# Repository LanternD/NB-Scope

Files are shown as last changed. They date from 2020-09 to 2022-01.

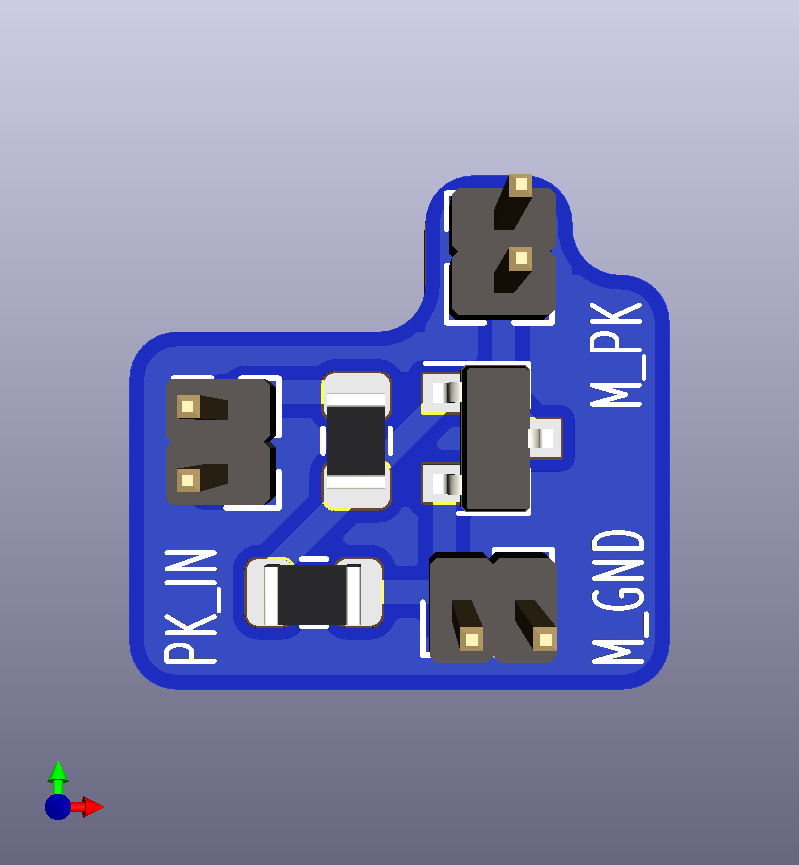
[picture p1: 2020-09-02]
Hardware/Auxilliary Boards/pwr_key_addon/pwr_key_addon.png

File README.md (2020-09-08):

# NB-Scope

Hardware and software design for NB-Scope.

NB-Scope is employed in our MobiCom 20 paper "Understanding Power Consumption of NB-IoT in the Wild: Tool and Large-scale Measuremen" [DOI](https://doi.org/10.1145/3372224.3419212).

Please check the README.md under the folders for more details.

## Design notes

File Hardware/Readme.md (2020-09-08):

# Hardware Guideline

## Overview

This folder contains the NB-Scope nodes hardware designs. Specifically, we have a folder for the mainboard, a folder for all the shieldboard for NB-Scope, and a folder for the auxilliary boards.

### Mainboard

The mainboard has 3 versions. **Please use ver 3.2**. The outdated versions are for reference only. They may work but not very stable. Ver 1.0 and 2.0 are not for NB-Scope projects, thus are omitted.

### Shieldboards

We have 7 types of shieldboard designs, supporting up to 9 types of different NB-IoT modules, including:

- Quectel BC28
- Quectel BC35
- Quectel BC26
- Quectel BC66
- Quectel BC95 (Not tested)
- Quectel BG36 (Not tested)
- Quectel BG96
- Gosuncn ME3616
- uBlox SARA-R410M-02B

(Quectel BG36/BG96 and Quectel BC35/BC95, have the same pin assignment, respectively.)

The module PCB project names should be straight-forward in the "Shieldboards" folder.

### Auxilliary boards

- Current sensing calibration board
- Firmware upgrade extension board
- Moulde benchmark extension board
- PWR_KEY addon

### Libraries

If you encounter missing symbol/footprint problem when opening the schematic or PCB files, please import them in the `Libraries` folder. The missing libraries should be a subset of the available footprints.

### Materials

I put the related documents related to hardware design here, including NB-IoT module summary and various datasheets.

## EDA environment

The software to open the projects is [KiCad](https://kicad-pcb.org/) (Pronounced as "key-cad").

PLEASE use the **Nightly-build** version of KiCad because the projects are created by that. The projects are not backward compatible.

To open the 3D viewer, click "View->3D Viewer" (<kbd>⌥+3</kbd> on Mac or <kbd>Alt+3</kbd> on other operating systems) in the `Pcbnew` software menu.

If you use the latest version of KiCad to open `.sch` files, `Eeschema`, the software component to edit schematic, will ask you to convert the `.sch` into `.kicad_sch`. Just go ahead and follow the instruction in KiCad.

You can generate all the files for fabrication in `Pcbnew` software module in KiCad.

## Project structure

- `<project_name>.pro`: project main file.
- `<project_name>.sch` or `<project_name>.kicad_sch`: project schematic design. If `.sch` and `.kicad_sch` co-exist, use the `.kicad_sch` one.
- `<project_name>.kicad_pcb`: project PCB design.
- `Exported Files` folder: exported/generated files from the projects, including Gerber files, bill of materials (BOM), positioning files (for SMT process), and other board 3D views or documents. I suggest you double check the project schematic and pcb designs, then generate these fabrication files again by yourself, instead of sending the Gerber files to manufacturers directly.

There are some KiCad generated backup or middle files. I forget to remove them before committing. You may ignore or edit them. They have the following patterns:

- `fp-info-cache`
- `<project name>-cache.lib`
- `<project name>-rescue.dcm`
- `<project name>-rescue.lib`
- `<project name>.kicad_pcb-bak`
- `<project name>.sch-bak`
- `sys-lib-table`

## Click into their corresponding folders for more details

If you have any questions, please send me an email to "yangdeli at msu.edu".

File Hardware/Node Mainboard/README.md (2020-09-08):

# Introduction

Node mainboard is responsible for hosting the module shieldboard, sensing the environment, collecting debug log and current traces, and so on.

Major components on the board: 

- STM32F103 as the main processor
- LM3671-3.3 as DC-DC converter
- CM1624 as micro SD card protector
- CAT24C128 as non-volatile memory
- TXB0108 as logic level converter (3.3v <-> 1.8v)
- Si7021 as temperature and relative humidity sensor
- INA226 as current sensor

It is powered by one or two 18650 batteries. It also supports USB 5V as the input voltage, using jumper cap to switch.

# Important Notes

## Components

- Pin headers. For the two rows hosting the NB-IoT UE shieldboard and the power jumpper, please use 1.27 mm pitch connectors. For all the other 1.27 mm throughhole connectors with 3-6 pins, use 1.25 mm pitch connectors. Please take a look at the photo of Ver 3.1 below. Please find the datasheet in "[Hardware/Materials](../Materials/A1251.pdf)" folder. Male connector: A1251H-XP; Female connector: A1251WV-XP. Note: this is just an example. You don't need to use the exact component.
- The 1.25mm pitch connectors could be converted to 2.54 mm pitch pins to connect to other components, such as ST-Link programmer.
- USB connector. There are many similar USB connectors available, please take a look at their size and shape and ensure they match. "Molex-105017-0001" would work but it is expensive. 
- Battery holder. One thing that is not shown in the picture is the battery holder, whose model is "BK-18650-PC4". You need to solder this **after everything else**, because the battery holder will block the access to whole bottom layer.

## NB-IoT UE Pin Assignment

The pin assignment should be taken care for future module shieldboard design.

Module Pin Assignment

Note: the labels starting with `M_` means the pins are treated as part of the module. For example, `M_MAIN_UART_TX` means the UART Tx of the module, which should be connected to the MCU UART Rx pin accordingly.

`Left_Conn` means the upper row in the picture below, `Right_conn` is the bottom row accordingly.

The module ground GNDs are aggregated to 4 pins on the `Right_conn`, which passes through a current sampling resistor on the mainboard.

# Known Issues

- If you use the generic ST-Link V2 dongle as programmer, do not use it to power the board alone, otherwise the LM3671 buck converter chip will burn. 

  **Correct way**: Power on the board using 18650 battery or 5V USB, then plug on the ST-Link debugger. After you finish programming/debugging, unplug ST-Link V2 FIRST, and then shutdown the board power.

- I didn't add the ESD protection to the board, so please ensure the ESD on the hand is largely removed before touching the board.

**Note**: Ver 3.1 and 3.0 have other minor issues, which were largely fixed in Ver 3.2. Please see the "Change Log" below. To save your time, do not use Ver 3.0 and 3.1.

- The "Module USB" can use as the 5V input of the board, while the "MCU USB" cannot do it. If you want to use the latter one to power the board, connect the "+5V" near it to the "+5V" near the "PWR SELECT" pin header.

# Suggestions in Mainboard Hardware Design

The latest version (ver 3.2) of mainboard generally works well, but I have several important suggestions for future design. 

1. Upgrade the power chip. LM3671 supports a maximum current of 600 mA, which sometimes has little margin for some NB-IoT modules. So I suggest using other power IC, such as LM3281 or TPS62160.
2. The STM32F103 does not have DMA channel for SD card writing, which means you cannot do anything else when writing the SD card. My suggestion is to use another STM32 chip. You need to double check in STM32 CubeMX whether the chip supports DMA channel in SDIO interface.
3. Add the ESD protection circuit.
4. Add a fuse to the power module.

# Gallery

## Ver 3.2

Node Mainboard v3.2
Node Mainboard v3.2

Note: the two shieldboard rows should be pin socket, instead of pin header. They are interchangeable though.

## Ver 3.1

Node Mainboard v3.1
Node Mainboard v3.1
Node Mainboard v3.1

## Ver 3.0

Node Mainboard v3.0
Node Mainboard v3.0

# Change Log

## Ver 3.2

- Added a DTC143Z to control the PWRKEY pin for uBlox SARA-R410M-02B and Quectel BG96, BC26, and BC66, such that we don't need the `pwr_key_add_on` modification board for these modules.
- Replaced the labels in schematic by another type (with an enclosure), which shows the direction of the signal.
- Added a power jumper to isolate the DC-DC module with other components on the board, for easier debugging.
- Used a smaller form factor transistor (DTC143Z) for LED control.
- Added a 1.5k pull-up resistor for USB connector.
- Removed the BOOT0 control header. Connected BOOT0 to GND by default. Added a pad for connecting to 3.3V by jumper wire temporarily. 
- Used a better matching footprint for all the buttons.
- Reduced the SWD connector from 6 pins to 4 pins.

## Ver 3.1

- Updated the power module. Replaced the large inductor to a smaller one. The power module layout was also improved.
- Replaced the resistor array in micro SD card protetion circuit with CM1624.
- Updated the layout of the user buttons.

## Ver 3.0

Actually the first version of NB-Scope mainboard.

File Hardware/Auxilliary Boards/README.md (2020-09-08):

# Introduction

Auxilliary boards are used to extend the capability of the mainboard and shieldboard, as well as to calibrate the current sensors.

# Current Calibration Board

Since the 0.1 Ohm current sensing resistors are different, the current sensing should be calibrated as per mainboard. 

You need a series of resistors for this board. The actual resistance does not matter. We just compare the sensor reading with the digital multimeter or power monitor reading.

## How to calibrate

calibration guide

Solder the 1.27 mm pitch headers according to the image above. Then follow the instruction to test the output.

Before calibration, make sure the embedded code runs the "current sensing demo" (`void run_demo8_i_bus_sensing()` in `Software/field-test-control/Src/fm_demo.c`). Check the `main.c` as well. 

The mainboard should be connected to the PC via USB, then the PC should open a serial console to read the data from the board.

Steps:

1. See the figure above.
2. See the figure above.
3. Read and record the external current measurement device output (mA).
4. Read and record the INA226 output via the USB UART. The board will output the current register reading once per second.
5. Repeat the above steps for resistors from 13.3 Ohm to 165 Ohm. The 11 Ohm is not recommended. Do not try the 5.6 Ohm.
6. Calculation as follows:
  
  1. Multiply the register value by 0.018311 to get the current reading of INA226. (Note: if the output is already the current value, you don't need to do this conversion, depending on the output of the embedded program.)
  2. Divide the INA226 current by the meter reading current to get a ratio.
  3. Multiply the ratio with 2778 (the preset INA226 calibration register value) to get the new calibration register value. 
  4. Average all the calibration values to get the final calibration value.
  
Here is a table showing the measurement and calculation example for one of our board.

| Expected current (mA) | Meter reading (mA) | INA226 register reading | Calculated INA226 current (mA) | New calibration value |
|-----------------------|--------------------|-------------------------|--------------------------------|-----------------------|
|                    20 |               20.0 |                    1089 |                      19.940679 |              2786.264 |
|                  48.5 |               49.0 |                    2659 |                      48.688949 |              2795.747 |
|                   100 |               99.5 |                    5484 |                     100.417524 |              2752.517 |
|                   150 |              149.0 |                    8235 |                     150.791085 |              2745.003 |
|                   200 |              198.0 |                   10974 |                     200.944914 |              2737.287 |
|                   248 |                244 |                   13487 |                     246.960457 |              2744.699 |

The final calibration value is the average of the last column, resulting in 2760.

The value you get should not be too far from these value above. The final calibration value is around 2700 - 2900. For the same batch of boards, the standard deviation is less than 50. If you use a different batch of current sensing resistor, the value can deviate up to 150. 

**The new current calibration value should be written into the onboard EEPROM before node deployment.**

Note: you need to calibrate EVERY mainboard.

# Module Benchmark Extension Board

An upgraded version of "Firmware Upgrade Extension Board". It docks the shieldboard for the "real-time benchmark mode" of NB-Scope. It can be used to upgrade the NB-IoT module firmware as well. Basically it pinouts all the necessary connectivity of the UE module, such that we can connect them to other peripherals, such as power monitor and UART. 

The two pin headers are compatible with the mainboard.

The "EXT3V3" is used to connect to the power monitor. For example, the RED terminal of the monitor is connected to the EXT3V3, and the BLACK terminal is connected to the 3V3, repectively. "EXTGND" is likewise.

# Firmware Upgrade Extension Board

This is the predecessor of "Module Benchmark Extension Board". Generally you can ignore this one.

# PWRKEY Addon

A tiny board that simply has a BJT on it. It is used to fixed the PWRKEY pin on the UE modules before ver 3.2 mainboard. If you use the latest version of the mainboard, you can ignore this.

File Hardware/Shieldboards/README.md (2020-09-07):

# Important Note

- The majority of the modules here can be soldered by hand, except Quectel BG96 and uBlox SARA-R410M-02B.
  - If you solder the SARA-R410M-02B **by yourself** (customizing the stencil and applying the solder paste), instead of using the SMT service, you need to shrink the size of all the pads of the SARA-R410M-02B footprint! Otherwise they are likely to get short-circuited.
  - Before
  
  SARA footprint before
  - After
  
  SARA footprint after
  
- All the shieldboards have a RESET button for the module.
- There is a design compatibility issue in those modules with a "PWR_KEY" pin, including SARA-R410M-02B, BG96, BC26, and BC66. The pin requires an open collector transistor to enable, which I use different hardware designs to take care of it across different version of the board. Here is the summary:
  - Node mainboard v3.2 + BC26/BC66/SARA shieldboard: no modification needed.
  - Node mainboard v3.2 + SARA shieldboard: use GPIO_L4 as the `PWRKEY` control pin. The software code can handle this.
  - Node mainboard v3.1 + BC26/BC66/BG96 shieldboard: need to fixed by the `pwr_key_addon` in "Auxilliary Boards" folder (**Not recommended**).
  - Node mainboard v3.1 + SARA shieldboard: use GPIO_L4 as the `PWRKEY` control pin (**Not recommended**).

# Photos

Note: the pin headers in the photos face up, but in reality they should be soldered on the other side of the board, facing down, such that the shieldboard can be docked to the mainboard.

## Quectel BC26 (BC66) Shieldboard

BC26 Shiledboard
BC26 Shiledboard

Note: BC66 is almost identical to BC26 board, except for the swap between UART Tx and Rx pin.

## Quectel BC28 Shieldboard

BC28 Shiledboard
BC28 Shiledboard

## Quectel BC95/BC35 Shieldboard

BC95 Shiledboard
BC95 Shiledboard

## Gosuncn ME3616 Shieldboard

ME3616 Shiledboard
ME3616 Shiledboard

## Quectel BG96/BG36 Shieldboard

BG96 Shiledboard
BG96 Shiledboard

## uBlox SARA-R410M-02B Shieldboard

SARA Shiledboard
SARA Shiledboard

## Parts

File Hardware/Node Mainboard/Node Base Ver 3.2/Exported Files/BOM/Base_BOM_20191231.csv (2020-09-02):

Id | Designator | Package | Quantity | Designation | Supplier and ref
1 | REF**,REF** | test_pad | 2 | test_pad
2 | REF** | WEEE-Logo_4.2x6mm_SilkScreen | 1 | WEEE-Logo_4.2x6mm_SilkScreen
3 | REF** | ESD-Logo_6.6x6mm_SilkScreen | 1 | ESD-Logo_6.6x6mm_SilkScreen
4 | U1 | SMF05C | 1 | SMF05C
5 | J6 | PinSocket_1x04_P1.27mm_Vertical | 1 | SWD_Conn
6 | H1 | 18650_Battery_Holder_2x | 1 | Battery_Holder_2x
7 | TP2 | test_pad | 1 | 3.3V_OUT
8 | TP1 | test_pad | 1 | 3.3VPU
9 | SW3 | SMD_Switch | 1 | SW_2
10 | SW2 | SMD_Switch | 1 | SW_1
11 | SW1 | SMD_Switch | 1 | SW_RST
12 | R15 | R_0603_1608Metric | 1 | 1.5k
13 | R4,R8,R7 | R_0603_1608Metric | 3 | 10k
14 | J2 | PinHeader_2x02_P1.27mm_Vertical | 1 | 3.3V ISO
15 | Q2,Q1 | SOT-723 | 2 | DTC143Z
16 | U8 | UDFN-16_3.3x1.35mm_0.4Pitch | 1 | CM1624
17 | REF** | test_pad | 1 | SW
18 | R14,R5 | R_0603_1608Metric | 2 | 0
19 | L1 | L_Sumida_CDRH2D14_3.2x3.2x1.55mm | 1 | 2.2uH
20 | C9 | C_0805_2012Metric | 1 | 10uF
21 | C8 | C_0805_2012Metric | 1 | 4.7uF
22 | G*** | Cat-Logo | 1 | LOGO
23 | C20,C19,C18,C16,C13,C12,C11,C10 | C_0603_1608Metric | 8 | 100nF
24 | Y1 | Crystal_SMD_5032-2Pin_5.0x3.2mm | 1 | 8MHz
25 | D1,D4,D3,D2 | LED_0805_2012Metric | 4 | LED
26 | J8 | PinHeader_1x03_P2.54mm_Vertical | 1 | PWR_SELECT
27 | J4 | PinSocket_1x04_P1.27mm_Vertical | 1 | Display_Connector
28 | R16,R13,R11,R3 | R_0603_1608Metric | 4 | 4.7k
29 | RN4 | R_Array_Convex_4x0603 | 1 | 2.2k
30 | U7 | USON-20_2x4mm_P0.4mm | 1 | TXB0108DQSR
31 | T1 | test_pad | 1 | M_ADC
32 | R21,R20,R10,R9 | R_0603_1608Metric | 4 | 22
33 | R2 | R_0603_1608Metric | 1 | 470k
34 | R1 | R_0603_1608Metric | 1 | 220k
35 | J10,J5 | USB_Micro-B_Molex-105017-0001 | 2 | USB_B_Micro
36 | J9 | PinSocket_1x03_P1.27mm_Vertical | 1 | AUX_UART
37 | J7 | PinSocket_1x06_P1.27mm_Vertical | 1 | GPIO_Out
38 | J3 | TF_Card_Socket | 1 | Micro_SD_Card
39 | C17,C15,C14,C7,C1 | C_0603_1608Metric | 5 | 10nF
40 | C5,C4,C3,C2 | C_0603_1608Metric | 4 | 10pF
41 | Y2 | Crystal_SMD_3215-2Pin_3.2x1.5mm | 1 | 32.768kHz
42 | U6 | DFN-6-1EP_3x3mm_P1mm_EP1.5x2.4mm | 1 | Si7021-A20
43 | U5 | VSSOP-10_3x3mm_P0.5mm | 1 | INA226
44 | U4 | TSOT-23-5 | 1 | LM3671MF-3.3
45 | U3 | SOIC-8_3.9x4.9mm_P1.27mm | 1 | CAT24C128
46 | U2 | LQFP-64_10x10mm_P0.5mm | 1 | STM32F103RETx
47 | R12 | R_1206_3216Metric | 1 | R100
48 | J13 | PinHeader_1x22_P1.27mm_Vertical | 1 | Right_Conn
49 | J12 | PinHeader_1x22_P1.27mm_Vertical | 1 | Left_Conn
50 | J1 | Nano Sim Socket 1.1H, 6P | 1 | SIM_Card

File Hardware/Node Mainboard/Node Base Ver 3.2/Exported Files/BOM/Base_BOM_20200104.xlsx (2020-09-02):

Id | Need Soldering | Unit Price | Price for one Board | Designator | Package | Quantity | Designation | Supplier and ref | Datasheet
1 | N |  |  | REF**,REF** | test_pad | 2 | test_pad
2 | N |  |  | REF** | WEEE-Logo_4.2x6mm_SilkScreen | 1 | WEEE-Logo_4.2x6mm_SilkScreen
3 | N |  |  | REF** | ESD-Logo_6.6x6mm_SilkScreen | 1 | ESD-Logo_6.6x6mm_SilkScreen
4 | Y |  |  | U1 | SMF05C | 1 | SMF05C | SMF05CT1G
5 | N |  |  | J6 | PinSocket_1x04_P1.27mm_Vertical | 1 | SWD_Conn
6 | N |  |  | H1 | 18650_Battery_Holder_2x | 1 | Battery_Holder_2x
7 | N |  |  | TP2 | test_pad | 1 | 3.3V_OUT
8 | N |  |  | TP1 | test_pad | 1 | 3.3VPU
9 | Y |  |  | SW3 | SMD_Switch | 1 | SW_2 | TSA363G25-250B White_3*6*2.5 | https://item.szlcsc.com/330468.html
10 | Y |  |  | SW2 | SMD_Switch | 1 | SW_1 | TSA363G25-250H Red_3*6*2.5 | https://item.szlcsc.com/330467.html
11 | Y |  |  | SW1 | SMD_Switch | 1 | SW_RST | 1TS002B-1700-5001-CT | https://item.szlcsc.com/300328.html
12 | Y |  |  | R15 | R_0603_1608Metric | 1 | 1.5k
13 | Y |  |  | R4,R8,R7 | R_0603_1608Metric | 3 | 10k
14 | Y |  |  | J2 | PinHeader_2x02_P1.27mm_Vertical | 1 | 3.3V ISO | Trimmed from: | https://item.szlcsc.com/44374.html
15 | Y |  |  | Q2,Q1 | SOT-723 | 2 | DTC043ZM | DTC043ZMT2L | http://rohmfs.rohm.com/en/products/databook/datasheet/discrete/transistor/digital/dtc043zmt2l-e.pdf
16 | Y |  |  | U8 | UDFN-16_3.3x1.35mm_0.4Pitch | 1 | CM1624 | CM1624-08DE | https://www.mouser.com/ProductDetail/ON-Semiconductor/CM1624-08DE?qs=sGAEpiMZZMvbyeSUH4qH%2FG%252BWhnbEq2Sg
17 | N |  |  | REF** | test_pad | 1 | SW
18 | Y |  |  | R14,R5 | R_0603_1608Metric | 2 | 0
19 | Y |  |  | L1 | L_Sumida_CDRH2D14_3.2x3.2x1.55mm | 1 | 2.2uH | CDRH2D14NP-2R2NC | https://www.mouser.com/ProductDetail/851-CDRH2D14NP-2R2NC
20 | Y |  |  | C9 | C_0805_2012Metric | 1 | 10uF | JMK212BJ106KG-T
21 | Y |  |  | C8 | C_0805_2012Metric | 1 | 4.7uF | JMK212BJ475KG-T
22 | N |  |  | G*** | Cat-Logo | 1 | LOGO
23 | Y |  |  | C20,C19,C18,C16,C13,C12,C11,C10 | C_0603_1608Metric | 8 | 100nF
24 | Y |  |  | Y1 | Crystal_SMD_5032-2Pin_5.0x3.2mm | 1 | 8MHz | CX5032GA08000H0PST02
25 | Y |  |  | D1,D4,D3,D2 | LED_0805_2012Metric | 4 | LED | LTST-C170KRKT red | Color is flexible
26 | Y |  |  | J8 | PinHeader_1x03_P2.54mm_Vertical | 1 | PWR_SELECT |  | https://item.szlcsc.com/50265.html
27 | N |  |  | J4 | PinSocket_1x04_P1.27mm_Vertical | 1 | Display_Connector
28 | Y |  |  | R16,R13,R11,R3 | R_0603_1608Metric | 4 | 4.7k
29 | Y |  |  | RN4 | R_Array_Convex_4x0603 | 1 | 2.2k | CAY16-222J4LF
30 | Y |  |  | U7 | USON-20_2x4mm_P0.4mm | 1 | TXB0108DQSR | TXB0108DQSR
31 | N |  |  | T1 | test_pad | 1 | M_ADC
32 | Y |  |  | R21,R20,R10,R9 | R_0603_1608Metric | 4 | 22
33 | Y |  |  | R2 | R_0603_1608Metric | 1 | 470k
34 | Y |  |  | R1 | R_0603_1608Metric | 1 | 220k
35 | Y |  |  | J10,J5 | USB_Micro-B_Molex-105017-0001 | 2 | USB_B_Micro | Molex 105017-0001 | https://www.molex.com/webdocs/datasheets/pdf/en-us/1050170001_IO_CONNECTORS.pdf
36 | N |  |  | J9 | PinSocket_1x03_P1.27mm_Vertical | 1 | AUX_UART
37 | N |  |  | J7 | PinSocket_1x06_P1.27mm_Vertical | 1 | GPIO_Out
38 | Y |  |  | J3 | TF_Card_Socket | 1 | Micro_SD_Card | TF-015 | https://item.szlcsc.com/114441.html
39 | Y |  |  | C17,C15,C14,C7,C1 | C_0603_1608Metric | 5 | 10nF
40 | Y |  |  | C5,C4,C3,C2 | C_0603_1608Metric | 4 | 10pF
41 | Y |  |  | Y2 | Crystal_SMD_3215-2Pin_3.2x1.5mm | 1 | 32.768kHz | NX3215SA-32.768K-STD-MUS-2
42 | Y |  |  | U6 | DFN-6-1EP_3x3mm_P1mm_EP1.5x2.4mm | 1 | Si7021-A20 | SI7021-A20-GM1R
43 | Y |  |  | U5 | VSSOP-10_3x3mm_P0.5mm | 1 | INA226 | INA226AIDGSR
44 | Y |  |  | U4 | TSOT-23-5 | 1 | LM3671MF-3.3 | LM3671MF-3.3/NOPB
45 | Y |  |  | U3 | SOIC-8_3.9x4.9mm_P1.27mm | 1 | CAT24C128 | CAT24C128WI-GT3
46 | Y |  |  | U2 | LQFP-64_10x10mm_P0.5mm | 1 | STM32F103RETx | STM32F103RET6
47 | Y |  |  | R12 | R_1206_3216Metric | 1 | R100 | CRM1206AFX-R100ELF
48 | Y |  |  | J13 | PinSocket_1x22_P1.27mm_Vertical | 1 | Right_Conn | Can be trimmed from 1*50 etc. | Example https://item.taobao.com/item.htm?id=530374128662&ns=1&abbucket=18
49 | Y |  |  | J12 | PinSocket_1x22_P1.27mm_Vertical | 1 | Left_Conn | Can be trimmed from 1*50 etc. | Example https://item.taobao.com/item.htm?id=530374128662&ns=1&abbucket=18
50 | Y |  |  | J1 | Nano Sim Socket 1.1H, 6P | 1 | SIM_Card | Molex 104224-0820

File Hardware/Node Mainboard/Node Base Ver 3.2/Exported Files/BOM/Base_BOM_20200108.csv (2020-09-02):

Id | Designator | Package | Quantity | Designation | Supplier and ref
1 | U1 | SOT-363_SC-70-6 | 1 | SMF05C
2 | J13 | PinHeader_1x22_P1.27mm_Vertical | 1 | Right_Conn
3 | J12 | PinHeader_1x22_P1.27mm_Vertical | 1 | Left_Conn
4 | REF**,REF** | test_pad | 2 | test_pad
5 | REF** | WEEE-Logo_4.2x6mm_SilkScreen | 1 | WEEE-Logo_4.2x6mm_SilkScreen
6 | REF** | ESD-Logo_6.6x6mm_SilkScreen | 1 | ESD-Logo_6.6x6mm_SilkScreen
7 | J6 | PinSocket_1x04_P1.27mm_Vertical | 1 | SWD_Conn
8 | H1 | 18650_Battery_Holder_2x | 1 | Battery_Holder_2x
9 | TP2 | test_pad | 1 | 3.3V_OUT
10 | TP1 | test_pad | 1 | 3.3VPU
11 | SW3 | SMD_Switch | 1 | SW_2
12 | SW2 | SMD_Switch | 1 | SW_1
13 | SW1 | SMD_Switch | 1 | SW_RST
14 | R15 | R_0603_1608Metric | 1 | 1.5k
15 | R4,R8,R7 | R_0603_1608Metric | 3 | 10k
16 | J2 | PinHeader_2x02_P1.27mm_Vertical | 1 | 3.3V ISO
17 | Q2,Q1 | SOT-723 | 2 | DTC143Z
18 | U8 | UDFN-16_3.3x1.35mm_0.4Pitch | 1 | CM1624
19 | REF** | test_pad | 1 | SW
20 | R14,R5 | R_0603_1608Metric | 2 | 0
21 | L1 | L_Sumida_CDRH2D14_3.2x3.2x1.55mm | 1 | 2.2uH
22 | C9 | C_0805_2012Metric | 1 | 10uF
23 | C8 | C_0805_2012Metric | 1 | 4.7uF
24 | G*** | Cat-Logo | 1 | LOGO
25 | C20,C19,C18,C16,C13,C12,C11,C10 | C_0603_1608Metric | 8 | 100nF
26 | Y1 | Crystal_SMD_5032-2Pin_5.0x3.2mm | 1 | 8MHz
27 | D1,D4,D3,D2 | LED_0805_2012Metric | 4 | LED
28 | J8 | PinHeader_1x03_P2.54mm_Vertical | 1 | PWR_SELECT
29 | J4 | PinSocket_1x04_P1.27mm_Vertical | 1 | Display_Connector
30 | R16,R13,R11,R3 | R_0603_1608Metric | 4 | 4.7k
31 | RN4 | R_Array_Convex_4x0603 | 1 | 2.2k
32 | U7 | USON-20_2x4mm_P0.4mm | 1 | TXB0108DQSR
33 | T1 | test_pad | 1 | M_ADC
34 | R21,R20,R10,R9 | R_0603_1608Metric | 4 | 22
35 | R2 | R_0603_1608Metric | 1 | 470k
36 | R1 | R_0603_1608Metric | 1 | 220k
37 | J10,J5 | USB_Micro-B_Molex-105017-0001 | 2 | USB_B_Micro
38 | J9 | PinSocket_1x03_P1.27mm_Vertical | 1 | AUX_UART
39 | J7 | PinSocket_1x06_P1.27mm_Vertical | 1 | GPIO_Out
40 | J3 | TF_Card_Socket | 1 | Micro_SD_Card
41 | C17,C15,C14,C7,C1 | C_0603_1608Metric | 5 | 10nF
42 | C5,C4,C3,C2 | C_0603_1608Metric | 4 | 10pF
43 | Y2 | Crystal_SMD_3215-2Pin_3.2x1.5mm | 1 | 32.768kHz
44 | U6 | DFN-6-1EP_3x3mm_P1mm_EP1.5x2.4mm | 1 | Si7021-A20
45 | U5 | VSSOP-10_3x3mm_P0.5mm | 1 | INA226
46 | U4 | TSOT-23-5 | 1 | LM3671MF-3.3
47 | U3 | SOIC-8_3.9x4.9mm_P1.27mm | 1 | CAT24C128
48 | U2 | LQFP-64_10x10mm_P0.5mm | 1 | STM32F103RETx
49 | R12 | R_1206_3216Metric | 1 | R100
50 | J1 | Nano Sim Socket 1.1H, 6P | 1 | SIM_Card

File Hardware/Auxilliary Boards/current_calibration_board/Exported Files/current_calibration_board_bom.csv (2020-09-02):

Id | Designator | Package | Quantity | Designation | Supplier and ref
1 | REF** | KiCad-Logo2_5mm_SilkScreen | 1 | KiCad-Logo2_5mm_SilkScreen
2 | G*** | Cat-Logo | 1 | LOGO
3 | J6 | PinHeader_1x03_P2.54mm_Vertical | 1 | GND_Conn
4 | R8 | Resistor_SMD_1225_2W | 1 | 5.6
5 | R7 | R_2512_6332Metric_Pad1.52x3.35mm_HandSolder | 1 | 11
6 | R6 | R_2512_6332Metric_Pad1.52x3.35mm_HandSolder | 1 | 13.3
7 | R5 | R_2512_6332Metric_Pad1.52x3.35mm_HandSolder | 1 | 16.5
8 | R4 | R_1210_3225Metric_Pad1.42x2.65mm_HandSolder | 1 | 22
9 | R3 | R_1210_3225Metric_Pad1.42x2.65mm_HandSolder | 1 | 33
10 | R2 | R_1206_3216Metric_Pad1.42x1.75mm_HandSolder | 1 | 68
11 | R1 | R_0805_2012Metric_Pad1.15x1.40mm_HandSolder | 1 | 165
12 | J5 | PinHeader_1x08_P2.54mm_Vertical | 1 | Conn_01x08
13 | J4 | PinHeader_1x03_P2.54mm_Vertical | 1 | Vcc_Conn
14 | J3 | PinHeader_1x04_P1.27mm_Vertical | 1 | GND_Conn
15 | J2,J1 | PinHeader_1x03_P1.27mm_Vertical | 2 | Vcc_Conn

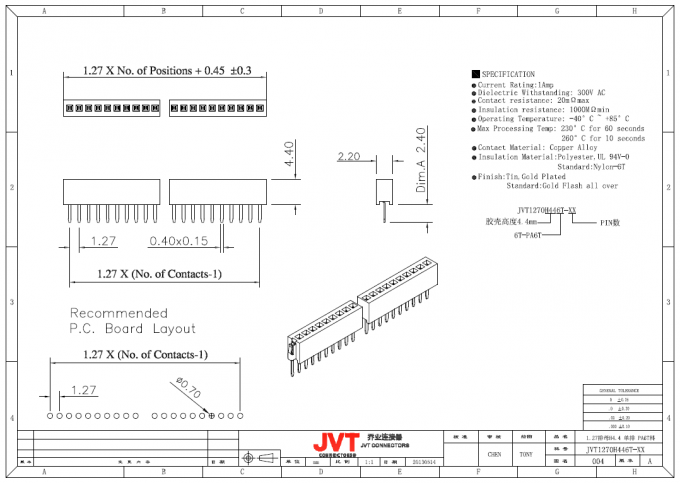
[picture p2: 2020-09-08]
Hardware/Materials/1.27 pin socket.png

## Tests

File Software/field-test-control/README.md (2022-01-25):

# Field Test Control

Embedded code that runs on STM32F103RET6, hosting a bunch of peripherals. It performs the NB-IoT field measurement task.

Note: the "`fm_`" in the code means "field measurement".

# MCU Software version log

- 00001: 20200111. Code is ready for BC28/BC26/ME3616. Migrating to BG96.
- 00002:

# Design 

## MCU

- STM32F103RETx. 72MHz 512kB Flash, 64kB RAM.
- High speed external (HSE) crystal oscillator: 8MHz, cap: 10 pF.
- LSE crystal oscillator: 32.768kHz, cap: 10 pF, high quality ceramic cap.
- No pull-up resistor needed for **RESET**.
- I2C pull-up resistor = 4.7 kOhm.
- SDIO freq max: 48 MHz.

### Pin Connection

- TF (SDIO)

	39 PC8 <-> TF 7 SDIO_D0
	40 PC9 <-> TF 8 SDIO_D1
	51 PC10 <-> TF 1 SDIO_D2
	52 PC11 <-> TF 2 SDIO_D3
	53 PC12 <-> TF 5 SDIO_CLK
	54 PD2 <-> TF 3 SDIO_CMD

- SWD (MCU debug port)

	46 PA13 SWD_IO <-> SWD_IO
	49 PA14 SWD_CLK<-> SWD_CLK
	55 PB3 SWO <-> SWO

- Temperature & humidity sensor, EEPROM (share the same I2C)

  29 PB10 I2C2_SCL <-> Si7021 Sensor_SCL, EEPROM_SCL
  30 PB11 I2C2_SDA <-> Si7021 Sensor_SDA, EEPROM_SDA

- INA226 current sensor

  58 PB6 I2C1_SCL <-> INA226_SCL
  59 PB7 I2C1_SDA <-> INA226_SDA

- MCU USB

  44 PA11 USBDM <-> Connector USB DM
  45 PA12 USBDP <-> Connector USB DP

- Misc.

16 PA2 USART2_Tx <-> Module Main UART Rx
17 PA3 USART2_Rx <-> Module Main UART Tx
42 PA9 USART1_Tx <-> Module Debug UART Rx
43 PA10 USART1_Rx <-> Module Debug UART Tx

8 PC0 ADC123_IN10 <-> V_batt ADC

33 PB12 SPI2_NSS <-> Module SPI_CS
34 PB13 SPI2_SCK <-> Module SPI_CLK / I2S_CK
35 PB14 SPI2_MISO <-> Module SPI2_MISO
36 PB15 SPI2_MOSI <-> Module SPI2_MOSI

9 PC1 <-> GPIO_L1
10 PC2 <-> PSM_IND
11 PC3 <-> GPIO_L2
14 PA0 <-> GPIO_L3
15 PA1 <-> GPIO_L4
20 PA4 <-> Module PWRKEY
21 PA5 <-> Module RESET
22 PA6 <-> Module PSM external wakeup interruption
23 PA7 <-> AP_READY
50 PA15 <-> GPIO_R1
41 PA8 <-> GPIO_R2
38 PC7 <-> GPIO_R3
37 PC6 <-> Module RI

- Not used by module:

26 PB0 <-> SWITCH_1
27 PB1 <-> SWITCH_2
56 PB4 <-> TF_DETECT (Ext GPIO_1)
57 PB5 <-> Ext GPIO_2
61 PB8 <-> Ext GPIO_3
62 PB9 <-> Ext GPIO_4
24 PC4 <-> LED 0 on board
25 PC5 <-> LED 1 on board
2 PC13 <-> Not Connected

### Logic Convertion on Base Board

- Main UART Tx/Rx
- AUX UART Tx/Rx
- Debug UART Tx/Rx
- RI

### I2C Address

- INA226: 7 byte address is 0x80. with I2C1
- SI7021: 7 byte address is 0x40. with I2C2. After adding the r/w bit, should be 0x81 and 0x80;
- CAT24C128: 7 byte address is 0x54. with I2C2.
- SSD1306 display: 7 byte address is 0x78. with I2C2.

### EEPROM Storage Design

There are 256 pages available, 64 Bytes each. So the total capacity is 256\*64 = 16382 Bytes = 128 Kbits.

- Global Variables:
	- Last running mode

- Demo page
	- 0x2000 - 0x2003: uint32_t wakeup times from sleeping.
	- 0x2004 - 0x2004: uint8_t seconds to sleep (for RTT configuration).

## TF Card

Need pull-up 25 kOhm, serial 40 Ohm: CLK, CMD, Data0, Data1, Data2, Data3

Convex resistor array CAY16-223J8LF

# Current Sensing INA226

- Use Kelven connection!
- LSB for shunt voltage: fixed 2.5 uV.
- Calculation example:
	- Current LSB value = 0.8/2^15 = 0.000024414 = 24.414 uA
	- Calibration registor = 0.00512/(CurrentLSB\*ShuntResistor) = 0.00512 / (0.000024414\*0.05) = 4194
	- Example: Assume current_truth = 0.2A, R_shunt=0.05 Ohm, then shunt voltage = 10mV. ShuntVReg = 10mV/2.5uV=4000. current_calc = ShuntV\*CalibrationReg/2048 = 4000\*4194/2048 \* Current LSB = 8191 \* Current LSB=8191\*0.000024414=0.199984 A.
- Choose 100 mOhm resistor.

## Current sensing calibration

As the shunt resistor has resistant variation, we need to calibrate it. Here's how to get the calibration register value:

- The shunt resistor on board is 100 mOhm.
- Determine the max possible current: I_max = 0.6A
- Calculate the current LSB: current_lsb = I_max / 2^15 = 0.6/2^15 = **0.018311** mA/bit <= **Fix this number!**
- According to the 7.5.1 Eq(3) in the datasheet: CurrentRegister = ShuntVoltage * CalibrationReg / 2048
- I_acutal = CurrentRegister * current_lsb
- Accoarding to Eq(1), calbirationReg_theoretical = 0.00512 / (current_lsb*R_shunt) = 0.00512 / (0.018311/1000*0.1) = 2796.1
- **Assume** the calibrationReg = 2778 (according to the calibration measurement on an actual circuit board)
- CalibrationReg_New / CalibrationReg_Old (which is 2778) = multimeter_current_reading / current_reading_from_INA226 = multimeter_current_reading / (CurrentReg_Old * current_lsb)
- **Example**: CurrentReg (use USB VCP to check) is 13543, Multiply this by 0.018311, you get an INA226 current reading = 248 mA. Next, the multimeter reading is 246.0 mA. So 248/246 = CalibrationReg_New/2778 => we have CalibrationReg_New = 2778*248/246 = 2800.
- Update INA226_CALIB_VAL in ti_ina226.h Line32 with the new caibration register 2800
- Check that the new current reading is more accurate.

# Modules

- Need to convert 3.3v to 1.8v (bidirectional): BC26, BC66, BG96, SARA R410M 02B
- Need to convert 3.3v to 3.0v (bidirectional): BC28, BC35, BC95
- Left side: 16 pins
- Right side: 10 pins

# Programming Task Lists

- RTT clock signal configuration
- [x] Battery voltage sensing
- Sleep and wake-up
- Watch-dog
- Temperature and humidity sensor reading
- [x] EEPROM writing and reading (share the same I2C with the sensor)
- Current sensing
- TF card read/write through SDIO
- AT Command control API
- Server configuration
- Debug log reading
- Debug log FSM
- (\*) DMA: current I2C to SDIO

------

# Links

- current sensor resistors

	[10 mOhm](https://www.mouser.com/ProductDetail/ROHM-Semiconductor/PMR100HZPFU10L0?qs=sGAEpiMZZMtlleCFQhR%2FzZdCyObyGWxusWWJKncYy0Q%3D)
	[100 mOhm](https://www.mouser.com/ProductDetail/Bourns/CRM1206AFX-R100ELF?qs=sGAEpiMZZMtlleCFQhR%2FzXAGiOCRCr1IaXP90uykHS56ie6t3FxO7w%3D%3D)

- tf card socket

	http://www.klsele.com/products/connectors/641/4975.html

- Resistor array 8X

	- [8X 22kOhm](https://www.mouser.com/ProductDetail/Bourns/CAY16-223J8LF?qs=sGAEpiMZZMvrmc6UYKmaNe77kisCPsGdUuiwPEa9T%2FU%3D)
	- [4X 2.2kOhm](https://www.mouser.com/ProductDetail/Bourns/CAY16-222J4LF?qs=sGAEpiMZZMvrmc6UYKmaNUApqJ%252B%2FEZrJ%2FpdW56SM27Q%3D)
	- [8X 43 Ohm](https://www.mouser.com/ProductDetail/Bourns/CAY16-430J4LF?qs=sGAEpiMZZMukHu%252BjC5l7YZZvIpUe0TuoDMVA%252BgU2smk%3D)

- 8MHz Crystal Oscillator

	https://detail.tmall.com/item.htm?spm=a230r.1.14.11.6bc4917d8fGEWE&id=36990674059&cm_id=140105335569ed55e27b&abbucket=13

# Future

- [x] Replace the pull-up resistors and protection circuits for SD card with On Semiconductor **CM1624**.
- [x] Redesign the 3.3 V converter circuit.
- [ ] Isolate the 3.3 V power output with the circuit power (with a jumper cap).
- [ ] Add a 1.5k pull-up resistor at MCU USB D+. (Must Have)
- [ ] The PWR_KEY pin should not go though the TXB0108. Move this part to the base board with a transistor.

# Module Board

[Impedance Calculator](https://chemandy.com/calculators/coplanar-waveguide-with-ground-calculator.htm)

Fr4 material. Relative permittivity=4.4. The board thickness is chosen as 1 mm. The trace thickness is 1.35 mil for 1oz copper. 

Microstrip: the trace width should be **1.83~1.87** mm.
Coplanar: the gap width should be **0.3 mm**, the track width is **1.29 mm**.

# Module specific AT commands

## BG96

- Set once
    + Scan sequence
        * AT+QCFG="nwscanmode",3,1
        * AT+QCFG="iotopmode",1,1
        * AT+QCFG="band",1,1,180A,11

- AT+QPSMS?
    + +QPSMS: 1,,,"46800","2880"  // network side parameters.

## SARA R410M-02B 

GPIO assignment: 

- Pin16, M_NET_LED
- Pin19, SARA_GPIO1
- Pin23, SARA_GPIO2
- Pin24, SARA_GPIO3
- Pin25, SARA_STATUS_LED
- Pin42, SIM_DET

AT Command

These command is needed for only **ONCE**.

- Set pin function (Page 168)
  - AT+UGPIOC=16,2
  - AT+UGPIOC=25,10
  - AT+UGPIOC=42,7
  
- Set searchable bands (reboot to take effect)
  - AT+UBANDMASK=0,0,0
  - AT+UBANDMASK=1,6154,0 (only search Band 2, 4, 12, 13)
  
- Select RAT
  - AT+URAT=8 // NB-IoT only

- PDP context definition

  - 

- PSM setting
    + AT+CPSMS=1,,,"00101100","00000001"  // For all the USA modules. (except BC66)
    + 12 hours PSM, 2 seconds idle.
    + Default: +CPSMS:0,,,"00011000","00001010"
    
The belows need to be set every round.

- Cell Info (Not supported)

  - AT+UCGED=5
  - AT+UCGED?

# BC66

- Set the CGDEFCONT (PDP context)
  - AT+QCGDEFCONT="IP","mw01.vzwstatic"  // for new models

Default CPSMS: +CPSMS: 1,,,"00100011","00100010"
  - AT+CPSMS=1,,,"00100011","00100010"  // This is the default
  - AT+CPSMS=1,,,"00100011","00000101"  // new: idle 10 seconds.

- Set baudrate
    + AT+IPR=115200  // fixed rate
    + AT&W  // write to NVM

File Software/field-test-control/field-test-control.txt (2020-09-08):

Configuration	field-test-control
STM32CubeMX 	5.4.0
Date	09/08/2020
MCU	STM32F103RETx

PERIPHERALS	MODES	FUNCTIONS	PINS
ADC1	IN10	ADC1_IN10	PC0
I2C1	I2C	I2C1_SCL	PB6
I2C1	I2C	I2C1_SDA	PB7
I2C2	I2C	I2C2_SCL	PB10
I2C2	I2C	I2C2_SDA	PB11
RCC	Crystal/Ceramic Resonator	RCC_OSC_IN	PD0-OSC_IN
RCC	Crystal/Ceramic Resonator	RCC_OSC_OUT	PD1-OSC_OUT
RCC	Crystal/Ceramic Resonator	RCC_OSC32_IN	PC14-OSC32_IN
RCC	Crystal/Ceramic Resonator	RCC_OSC32_OUT	PC15-OSC32_OUT
RTC	Activate Clock Source	RTC_VS_RTC_Activate	VP_RTC_VS_RTC_Activate
SDIO	SD 4 bits Wide bus	SDIO_CK	PC12
SDIO	SD 4 bits Wide bus	SDIO_CMD	PD2
SDIO	SD 4 bits Wide bus	SDIO_D0	PC8
SDIO	SD 4 bits Wide bus	SDIO_D1	PC9
SDIO	SD 4 bits Wide bus	SDIO_D2	PC10
SDIO	SD 4 bits Wide bus	SDIO_D3	PC11
SPI2	Full-Duplex Master	SPI2_MISO	PB14
SPI2	Full-Duplex Master	SPI2_MOSI	PB15
SPI2	Full-Duplex Master	SPI2_SCK	PB13
SYS	Serial Wire	SYS_JTCK-SWCLK	PA14
SYS	Serial Wire	SYS_JTMS-SWDIO	PA13
SYS	SysTick	SYS_VS_Systick	VP_SYS_VS_Systick
USART1	Asynchronous	USART1_RX	PA10
USART1	Asynchronous	USART1_TX	PA9
USART2	Asynchronous	USART2_RX	PA3
USART2	Asynchronous	USART2_TX	PA2
USB	Device (FS)	USB_DM	PA11
USB	Device (FS)	USB_DP	PA12

Pin Nb	PINs	FUNCTIONs	LABELs
3	PC14-OSC32_IN	RCC_OSC32_IN	
4	PC15-OSC32_OUT	RCC_OSC32_OUT	
5	PD0-OSC_IN	RCC_OSC_IN	
6	PD1-OSC_OUT	RCC_OSC_OUT	
8	PC0	ADC1_IN10	V_BATT_ADC
9	PC1	GPIO_Output	M_GPIO_L1
10	PC2	GPIO_Input	M_PSM_IND
11	PC3	GPIO_Output	M_GPIO_L2
14	PA0-WKUP	GPIO_Output	M_GPIO_L3
15	PA1	GPIO_Output	M_GPIO_L4
16	PA2	USART2_TX	
17	PA3	USART2_RX	
20	PA4	GPIO_Output	M_PWRKEY
21	PA5	GPIO_Output	M_RESET
22	PA6	GPIO_Output	M_WAKEUP_FROM_PSM
23	PA7	GPIO_Output	M_AP_READY
24	PC4	GPIO_Output	LED0
25	PC5	GPIO_Output	LED1
26	PB0	GPIO_EXTI0	BUTTON1
27	PB1	GPIO_EXTI1	BUTTON2
29	PB10	I2C2_SCL	BUS_SCL
30	PB11	I2C2_SDA	BUS_SDA
33	PB12	GPIO_Output	M_SPI_CS
34	PB13	SPI2_SCK	
35	PB14	SPI2_MISO	
36	PB15	SPI2_MOSI	
37	PC6	GPIO_Input	M_RI
38	PC7	GPIO_Output	M_GPIO_R3
39	PC8	SDIO_D0	
40	PC9	SDIO_D1	
41	PA8	GPIO_Output	M_GPIO_R2
42	PA9	USART1_TX	
43	PA10	USART1_RX	
44	PA11	USB_DM	
45	PA12	USB_DP	
46	PA13	SYS_JTMS-SWDIO	
49	PA14	SYS_JTCK-SWCLK	
50	PA15	GPIO_Output	M_GPIO_R1
51	PC10	SDIO_D2	
52	PC11	SDIO_D3	
53	PC12	SDIO_CK	
54	PD2	SDIO_CMD	
55	PB3*	SYS_JTDO-TRACESWO	
56	PB4	GPIO_Input	TF_DET
57	PB5	GPIO_Output	GPIO_2
58	PB6	I2C1_SCL	INA226_SCL
59	PB7	I2C1_SDA	INA226_SDA
61	PB8	GPIO_Output	GPIO_3
62	PB9	GPIO_Output	GPIO_4
PERIPHERALS	MODES	FUNCTIONS	PINS
ADC1	IN10	ADC1_IN10	PC0
I2C1	I2C	I2C1_SCL	PB6
I2C1	I2C	I2C1_SDA	PB7
I2C2	I2C	I2C2_SCL	PB10
I2C2	I2C	I2C2_SDA	PB11
RCC	Crystal/Ceramic Resonator	RCC_OSC_IN	PD0-OSC_IN
RCC	Crystal/Ceramic Resonator	RCC_OSC_OUT	PD1-OSC_OUT
RCC	Crystal/Ceramic Resonator	RCC_OSC32_IN	PC14-OSC32_IN
RCC	Crystal/Ceramic Resonator	RCC_OSC32_OUT	PC15-OSC32_OUT
RTC	Activate Clock Source	RTC_VS_RTC_Activate	VP_RTC_VS_RTC_Activate
SDIO	SD 4 bits Wide bus	SDIO_CK	PC12
SDIO	SD 4 bits Wide bus	SDIO_CMD	PD2
SDIO	SD 4 bits Wide bus	SDIO_D0	PC8
SDIO	SD 4 bits Wide bus	SDIO_D1	PC9
SDIO	SD 4 bits Wide bus	SDIO_D2	PC10
SDIO	SD 4 bits Wide bus	SDIO_D3	PC11
SPI2	Full-Duplex Master	SPI2_MISO	PB14
SPI2	Full-Duplex Master	SPI2_MOSI	PB15
SPI2	Full-Duplex Master	SPI2_SCK	PB13
SYS	Serial Wire	SYS_JTCK-SWCLK	PA14
SYS	Serial Wire	SYS_JTMS-SWDIO	PA13
SYS	SysTick	SYS_VS_Systick	VP_SYS_VS_Systick
USART1	Asynchronous	USART1_RX	PA10
USART1	Asynchronous	USART1_TX	PA9
USART2	Asynchronous	USART2_RX	PA3
USART2	Asynchronous	USART2_TX	PA2
USB	Device (FS)	USB_DM	PA11
USB	Device (FS)	USB_DP	PA12

Pin Nb	PINs	FUNCTIONs	LABELs
3	PC14-OSC32_IN	RCC_OSC32_IN	
4	PC15-OSC32_OUT	RCC_OSC32_OUT	
5	PD0-OSC_IN	RCC_OSC_IN	
6	PD1-OSC_OUT	RCC_OSC_OUT	
8	PC0	ADC1_IN10	V_BATT_ADC
9	PC1	GPIO_Output	M_GPIO_L1
10	PC2	GPIO_Input	M_PSM_IND
11	PC3	GPIO_Output	M_GPIO_L2
14	PA0-WKUP	GPIO_Output	M_GPIO_L3
15	PA1	GPIO_Output	M_GPIO_L4
16	PA2	USART2_TX	
17	PA3	USART2_RX	
20	PA4	GPIO_Output	M_PWRKEY
21	PA5	GPIO_Output	M_RESET
22	PA6	GPIO_Output	M_WAKEUP_FROM_PSM
23	PA7	GPIO_Output	M_AP_READY
24	PC4	GPIO_Output	LED0
25	PC5	GPIO_Output	LED1
26	PB0	GPIO_EXTI0	BUTTON1
27	PB1	GPIO_EXTI1	BUTTON2
29	PB10	I2C2_SCL	BUS_SCL
30	PB11	I2C2_SDA	BUS_SDA
33	PB12	GPIO_Output	M_SPI_CS
34	PB13	SPI2_SCK	
35	PB14	SPI2_MISO	
36	PB15	SPI2_MOSI	
37	PC6	GPIO_Input	M_RI
38	PC7	GPIO_Output	M_GPIO_R3
39	PC8	SDIO_D0	
40	PC9	SDIO_D1	
41	PA8	GPIO_Output	M_GPIO_R2
42	PA9	USART1_TX	
43	PA10	USART1_RX	
44	PA11	USB_DM	
45	PA12	USB_DP	
46	PA13	SYS_JTMS-SWDIO	
49	PA14	SYS_JTCK-SWCLK	
50	PA15	GPIO_Output	M_GPIO_R1
51	PC10	SDIO_D2	
52	PC11	SDIO_D3	
53	PC12	SDIO_CK	
54	PD2	SDIO_CMD	
55	PB3*	SYS_JTDO-TRACESWO	
56	PB4	GPIO_Input	TF_DET
57	PB5	GPIO_Output	GPIO_2
58	PB6	I2C1_SCL	INA226_SCL
59	PB7	I2C1_SDA	INA226_SDA
61	PB8	GPIO_Output	GPIO_3
62	PB9	GPIO_Output	GPIO_4

SOFTWARE PROJECT

Project Settings : 
Project Name : field-test-control
Project Folder : /Users/dlyang/Dropbox/field-test-control
Toolchain / IDE : SW4STM32
Firmware Package Name and Version : STM32Cube FW_F1 V1.8.0

Code Generation Settings : 
STM32Cube MCU packages and embedded software packs : Copy only the necessary library files
Generate peripheral initialization as a pair of '.c/.h' files per peripheral : No
Backup previously generated files when re-generating : No
Delete previously generated files when not re-generated : Yes
Set all free pins as analog (to optimize the power consumption) : No

Toolchains Settings : 
Compiler Optimizations :

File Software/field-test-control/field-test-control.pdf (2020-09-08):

## field-test-control Project Configuration Report

# 1. Description

## 1.1. Project

Project Name | field-test-control
Board Name | custom
Generated with: | STM32CubeMX 5.4.0
Date | 09/08/2020

## 1.2. MCU

MCU Series | STM32F1
MCU Line | STM32F103
MCU name | STM32F103RETx
MCU Package | LQFP64
MCU Pin number | 64

# 2. Pinout Configuration

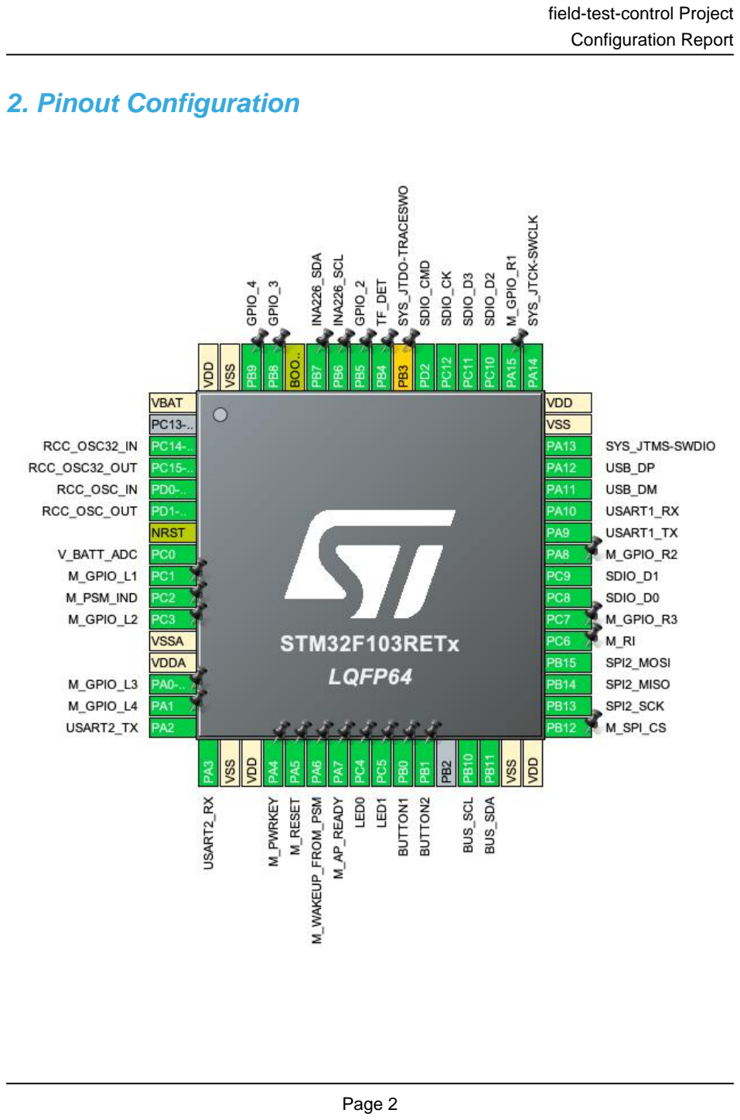
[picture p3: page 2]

# 3. Pins Configuration

Pin Number LQFP64 | Pin Name (function after reset) | Pin Type | Alternate Function(s) | Label
1 | VBAT | Power
3 | PC14-OSC32_IN | I/O | RCC_OSC32_IN
4 | PC15-OSC32_OUT | I/O | RCC_OSC32_OUT
5 | PD0-OSC_IN | I/O | RCC_OSC_IN
6 | PD1-OSC_OUT | I/O | RCC_OSC_OUT
7 | NRST | Reset
8 | PC0 | I/O | ADC1_IN10 | V_BATT_ADC
9 | PC1 * | I/O | GPIO_Output | M_GPIO_L1
10 | PC2 * | I/O | GPIO_Input | M_PSM_IND
11 | PC3 * | I/O | GPIO_Output | M_GPIO_L2
12 | VSSA | Power
13 | VDDA | Power
14 | PA0-WKUP * | I/O | GPIO_Output | M_GPIO_L3
15 | PA1 * | I/O | GPIO_Output | M_GPIO_L4
16 | PA2 | I/O | USART2_TX
17 | PA3 | I/O | USART2_RX
18 | VSS | Power
19 | VDD | Power
20 | PA4 * | I/O | GPIO_Output | M_PWRKEY
21 | PA5 * | I/O | GPIO_Output | M_RESET
22 | PA6 * | I/O | GPIO_Output | M_WAKEUP_FROM_PSM
23 | PA7 * | I/O | GPIO_Output | M_AP_READY
24 | PC4 * | I/O | GPIO_Output | LED0
25 | PC5 * | I/O | GPIO_Output | LED1
26 | PB0 | I/O | GPIO_EXTI0 | BUTTON1
27 | PB1 | I/O | GPIO_EXTI1 | BUTTON2
29 | PB10 | I/O | I2C2_SCL | BUS_SCL
30 | PB11 | I/O | I2C2_SDA | BUS_SDA
31 | VSS | Power
32 | VDD | Power
33 | PB12 * | I/O | GPIO_Output | M_SPI_CS
34 | PB13 | I/O | SPI2_SCK
35 | PB14 | I/O | SPI2_MISO
36 | PB15 | I/O | SPI2_MOSI
37 | PC6 * | I/O | GPIO_Input | M_RI
38 | PC7 * | I/O | GPIO_Output | M_GPIO_R3

Pin Number LQFP64 | Pin Name (function after reset) | Pin Type | Alternate Function(s) | Label
39 | PC8 | I/O | SDIO_D0
40 | PC9 | I/O | SDIO_D1
41 | PA8 * | I/O | GPIO_Output | M_GPIO_R2
42 | PA9 | I/O | USART1_TX
43 | PA10 | I/O | USART1_RX
44 | PA11 | I/O | USB_DM
45 | PA12 | I/O | USB_DP
46 | PA13 | I/O | SYS_JTMS-SWDIO
47 | VSS | Power
48 | VDD | Power
49 | PA14 | I/O | SYS_JTCK-SWCLK
50 | PA15 * | I/O | GPIO_Output | M_GPIO_R1
51 | PC10 | I/O | SDIO_D2
52 | PC11 | I/O | SDIO_D3
53 | PC12 | I/O | SDIO_CK
54 | PD2 | I/O | SDIO_CMD
55 | PB3 ** | I/O | SYS_JTDO-TRACESWO
56 | PB4 * | I/O | GPIO_Input | TF_DET
57 | PB5 * | I/O | GPIO_Output | GPIO_2
58 | PB6 | I/O | I2C1_SCL | INA226_SCL
59 | PB7 | I/O | I2C1_SDA | INA226_SDA
60 | BOOT0 | Boot
61 | PB8 * | I/O | GPIO_Output | GPIO_3
62 | PB9 * | I/O | GPIO_Output | GPIO_4
63 | VSS | Power
64 | VDD | Power

## * The pin is affected with an I/O function ** The pin is affected with a peripheral function but no peripheral mode is activated

# 4. Clock Tree Configuration

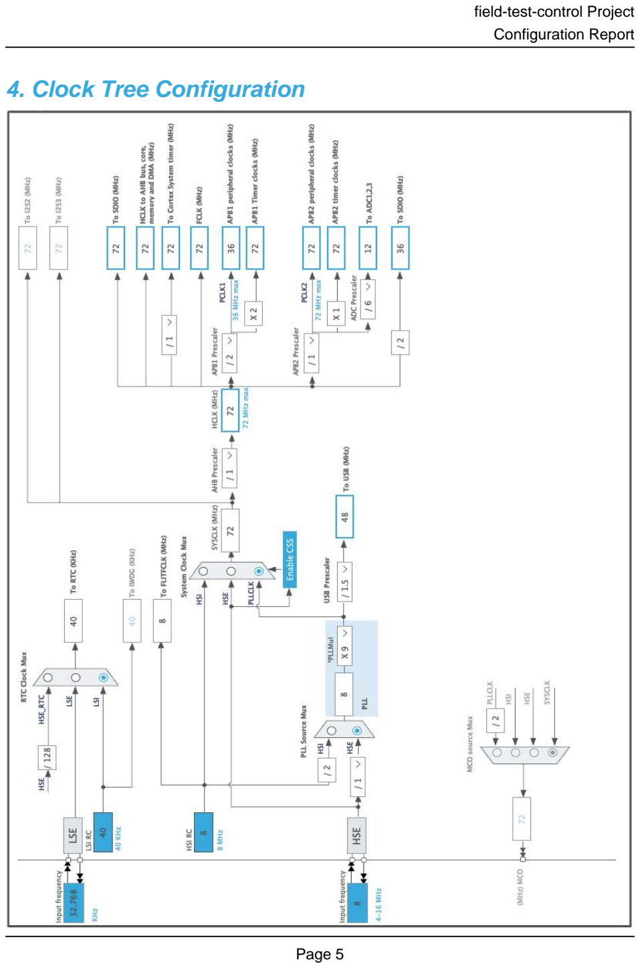
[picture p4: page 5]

# 5. Software Project

## 5.1. Project Settings

Name | Value
Project Name | field-test-control
Project Folder | /Users/dlyang/Dropbox/field-test-control
Toolchain / IDE | SW4STM32
Firmware Package Name and Version | STM32Cube FW_F1 V1.8.0

## 5.2. Code Generation Settings

Name | Value
STM32Cube MCU packages and embedded software | Copy only the necessary library files
Generate peripheral initialization as a pair of '.c/.h' files | No
Backup previously generated files when re-generating | No
Delete previously generated files when not re-generated | Yes
Set all free pins as analog (to optimize the power consumption) | No

# 6. Power Consumption Calculator report

### 6.1. Microcontroller Selection

Series | STM32F1
Line | STM32F103
MCU | STM32F103RETx
Datasheet | 14611_Rev12

### 6.2. Parameter Selection

Temperature | 25
Vdd | 3.3

# 7. IPs and Middleware Configuration

# 7.1. ADC1

## mode: IN10 7.1.1. Parameter Settings:

### ADCs_Common_Settings:

Mode | Independent mode

### ADC_Settings:

Data Alignment | Right alignment
Scan Conversion Mode | Enabled
Continuous Conversion Mode | Disabled
Discontinuous Conversion Mode | Disabled

### ADC_Regular_ConversionMode:

Enable Regular Conversions | Enable
Number Of Conversion | 4 *
External Trigger Conversion Source | Regular Conversion launched by software
Rank | 1
Channel | Channel 10
Sampling Time | 55.5 Cycles *
Rank | 2 *
Channel | Channel 10
Sampling Time | 1.5 Cycles
Rank | 3 *
Channel | Channel 10
Sampling Time | 1.5 Cycles
Rank | 4 *
Channel | Channel 10
Sampling Time | 1.5 Cycles

### ADC_Injected_ConversionMode:

Enable Injected Conversions | Disable

### WatchDog:

Enable Analog WatchDog Mode | false

# 7.2. GPIO

# 7.3. I2C1

## I2C: I2C 7.3.1. Parameter Settings:

### Master Features:

I2C Speed Mode | Fast Mode *
I2C Clock Speed (Hz) | 400000
Fast Mode Duty Cycle | Duty cycle Tlow/Thigh = 2

### Slave Features:

Clock No Stretch Mode | Disabled
Primary Address Length selection | 7-bit
Dual Address Acknowledged | Disabled
Primary slave address | 0
General Call address detection | Disabled

# 7.4. I2C2

## I2C: I2C 7.4.1. Parameter Settings:

### Master Features:

I2C Speed Mode | Fast Mode *
I2C Clock Speed (Hz) | 400000
Fast Mode Duty Cycle | Duty cycle Tlow/Thigh = 2

### Slave Features:

Clock No Stretch Mode | Disabled
Primary Address Length selection | 7-bit
Dual Address Acknowledged | Disabled
Primary slave address | 0
General Call address detection | Disabled

# 7.5. RCC

## High Speed Clock (HSE): Crystal/Ceramic Resonator Low Speed Clock (LSE) : Crystal/Ceramic Resonator 7.5.1. Parameter Settings:

### System Parameters:

VDD voltage (V) | 3.3
Prefetch Buffer | Enabled
Flash Latency(WS) | 2 WS (3 CPU cycle)

### RCC Parameters:

HSI Calibration Value | 16
HSE Startup Timout Value (ms) | 100
LSE Startup Timout Value (ms) | 5000

# 7.6. RTC

## mode: Activate Clock Source 7.6.1. Parameter Settings:

### Calendar Time:

Data Format | BCD data format

### General:

Auto Predivider Calculation | Enabled
Asynchronous Predivider value | Automatic Predivider Calculation Enabled
Output | Alarm pulse signal on the TAMPER pin

# 7.7. SDIO

## Mode: SD 4 bits Wide bus 7.7.1. Parameter Settings:

### SDIO parameters:

Clock transition on which the bit capture is made | Rising transition
SDIO Clock divider bypass | Disable
SDIO Clock output enable when the bus is idle | Disable the power save for the clock
SDIO hardware flow control | The hardware control flow is disabled
SDIOCLK clock divide factor | 0

# 7.8. SPI2

## Mode: Full-Duplex Master

## 7.8.1. Parameter Settings:

### Basic Parameters:

Frame Format | Motorola
Data Size | 8 Bits
First Bit | MSB First

### Clock Parameters:

Prescaler (for Baud Rate) | 2
Baud Rate | 18.0 MBits/s *
Clock Polarity (CPOL) | Low
Clock Phase (CPHA) | 1 Edge

### Advanced Parameters:

CRC Calculation | Disabled
NSS Signal Type | Software

# 7.9. SYS

## Debug: Serial Wire Timebase Source: SysTick

# 7.10. USART1

## Mode: Asynchronous 7.10.1. Parameter Settings:

### Basic Parameters:

Baud Rate | 921600 *
Word Length | 8 Bits (including Parity)
Parity | None
Stop Bits | 1

### Advanced Parameters:

Data Direction | Receive Only *
Over Sampling | 16 Samples

# 7.11. USART2

## Mode: Asynchronous

## 7.11.1. Parameter Settings:

### Basic Parameters:

Baud Rate | 9600 *
Word Length | 8 Bits (including Parity)
Parity | None
Stop Bits | 1

### Advanced Parameters:

Data Direction | Receive and Transmit
Over Sampling | 16 Samples

# 7.12. USB

## mode: Device (FS) 7.12.1. Parameter Settings:

### Basic Parameters:

Speed | Full Speed 12MBit/s

### Power Parameters:

Low Power | Disabled
Link Power Management | Disabled
Battery Charging | Disabled

# 7.13. FATFS

## mode: SD Card 7.13.1. Set Defines:

### Version:

FATFS version | R0.11

### Function Parameters:

FS_READONLY (Read-only mode) | Disabled
FS_MINIMIZE (Minimization level) | Disabled
USE_STRFUNC (String functions) | Enabled with LF -> CRLF conversion
USE_FIND (Find functions) | Disabled
USE_MKFS (Make filesystem function) | Enabled
USE_FASTSEEK (Fast seek function) | Enabled
USE_LABEL (Volume label functions) | Disabled

USE_FORWARD (Forward function) Disabled

### Locale and Namespace Parameters:

CODE_PAGE (Code page on target) | Simplified Chinese GBK (DBCS, OEM, Windows) *
USE_LFN (Use Long Filename) | Enabled with dynamic working buffer on the STACK *
MAX_LFN (Max Long Filename) | 255
LFN_UNICODE (Enable Unicode) | ANSI/OEM
STRF_ENCODE (Character encoding) | UTF-8
FS_RPATH (Relative Path) | Disabled

### Physical Drive Parameters:

VOLUMES (Logical drives) | 1
MAX_SS (Maximum Sector Size) | 512
MIN_SS (Minimum Sector Size) | 512
MULTI_PARTITION (Volume partitions feature) | Disabled
USE_TRIM (Erase feature) | Disabled
FS_NOFSINFO (Force full FAT scan) | 0

### System Parameters:

FS_TINY (Tiny mode) | Disabled
FS_NORTC (Timestamp feature) | Dynamic timestamp
NORTC_YEAR (Year for timestamp) | 2015
NORTC_MON (Month for timestamp) | 6
NORTC_MDAY (Day for timestamp) | 4
WORD_ACCESS (Platform dependent access option) | Byte access
FS_REENTRANT (Re-Entrancy) | Disabled
FS_TIMEOUT (Timeout ticks) | 1000
SYNC_t (O/S sync object) | osSemaphoreId
FS_LOCK (Number of files opened simultaneously) | 2

## 7.13.2. Advanced Settings:

### SDIO/SDMMC:

SDIO instance | SDIO
BSP code for SD | Generic

# 7.14. USB_DEVICE

## Class For FS IP: Communication Device Class (Virtual Port Com) 7.14.1. Parameter Settings:

### Basic Parameters:

USBD_MAX_NUM_INTERFACES (Maximum number of supported interfaces) | 1
USBD_MAX_NUM_CONFIGURATION (Maximum number of supported configuration) | 1
USBD_MAX_STR_DESC_SIZ (Maximum size for the string descriptors) | 512
USBD_SELF_POWERED (Enabled self power) | Enabled
USBD_DEBUG_LEVEL (USBD Debug Level) | 0: No debug message

### Class Parameters:

USB CDC Rx Buffer Size | 1000
USB CDC Tx Buffer Size | 1000

## 7.14.2. Device Descriptor:

### Device Descriptor:

VID (Vendor IDentifier) | 1155
LANGID_STRING (Language Identifier) | English(United States)
MANUFACTURER_STRING (Manufacturer Identifier) | MSDY Tech (USBCDC) *

### Device Descriptor FS:

PID (Product IDentifier) | 22336
PRODUCT_STRING (Product Identifier) | STM32 Virtual ComPort
CONFIGURATION_STRING (Configuration Identifier) | CDC Config
INTERFACE_STRING (Interface Identifier) | CDC Interface

### * User modified value

# 8. System Configuration

# 8.1. GPIO configuration

IP | Pin Signal GPIO mode | GPIO pull/up pull down

## Max Spee

d

## User Label

ADC1 | PC0 | ADC1_IN10 | Analog mode | n/a | n/a | V_BATT_ADC
I2C1 | PB6 | I2C1_SCL | Alternate Function Open Drain | n/a | High * | INA226_SCL
| PB7 | I2C1_SDA | Alternate Function Open Drain | n/a | High * | INA226_SDA
I2C2 | PB10 | I2C2_SCL | Alternate Function Open Drain | n/a | High * | BUS_SCL
| PB11 | I2C2_SDA | Alternate Function Open Drain | n/a | High * | BUS_SDA
RCC | PC14- OSC32_I N | RCC_OSC3 2_IN | n/a | n/a | n/a

PC15-
OSC32_
OUT

RCC_OSC3
2_OUT
n/a | n/a | n/a

PD0-
OSC_IN

RCC_OSC_
IN
n/a | n/a | n/a

PD1-
OSC_OU
T

RCC_OSC_
OUT
n/a | n/a | n/a
SDIO | PC8 | SDIO_D0 | Alternate Function Push Pull | n/a | High
| PC9 | SDIO_D1 | Alternate Function Push Pull | n/a | High
| PC10 | SDIO_D2 | Alternate Function Push Pull | n/a | High
| PC11 | SDIO_D3 | Alternate Function Push Pull | n/a | High
| PC12 | SDIO_CK | Alternate Function Push Pull | n/a | High
PD2 | SDIO_CMD Alternate Function
| | | Push Pull | n/a | High
SPI2 | PB13 | SPI2_SCK | Alternate Function Push Pull | n/a | High *
PB14 SPI2_MISO | Input mode | No pull-up and no pull-
| | | | down

n/a

PB15 SPI2_MOSI Alternate Function

| | | Push Pull | n/a | High *
SYS | PA13 | SYS_JTMS- | n/a | n/a | n/a

IP | Pin Signal GPIO mode | GPIO pull/up pull down

## Max Spee

d

## User Label

SWDIO
PA14 SYS_JTCK-SWCLK
| | | n/a | n/a | n/a
USART1 | PA9 | USART1_T X | Alternate Function Push Pull | n/a | High *

PA10 USART1_R

| | X | Input mode | No pull-up and no pull- down
n/a
USART2 | PA2 | USART2_T X | Alternate Function Push Pull | n/a | High *
| PA3 | USART2_R X | Input mode | No pull-up and no pull- down
n/a
USB | PA11 | USB_DM | n/a | n/a | n/a
| PA12 | USB_DP | n/a | n/a | n/a
Single Mapped Signals | PB3 | SYS_JTDO- TRACESW O | n/a | n/a | n/a
GPIO | PC1 | GPIO_Outp
ut

Output Push Pull No pull-up and no pulldown

Low | M_GPIO_L1
PC2 | GPIO_Input | Input mode | No pull-up and no pull-
down
n/a | M_PSM_IND
PC3 | GPIO_Outp
ut

Output Push Pull No pull-up and no pulldown

Low M_GPIO_L2

PA0-
WKUP

GPIO_Outp
ut

Output Push Pull No pull-up and no pulldown

Low | M_GPIO_L3
PA1 | GPIO_Outp
ut

Output Push Pull No pull-up and no pulldown

Low | M_GPIO_L4
PA4 | GPIO_Outp
ut
Output Push Pull | Pull-up * | Low | M_PWRKEY
PA5 | GPIO_Outp
ut
Output Push Pull | Pull-up * | Low | M_RESET
PA6 | GPIO_Outp
ut

Output Push Pull No pull-up and no pulldown

Low M_WAKEUP_FROM
_PSM
PA7 GPIO_Outp
ut

Output Push Pull No pull-up and no pulldown

Low | M_AP_READY
PC4 | GPIO_Outp
ut

Output Push Pull No pull-up and no pulldown

Low | LED0
PC5 | GPIO_Outp
ut

Output Push Pull No pull-up and no pulldown

Low | LED1
PB0 | GPIO_EXTI
0

### External Interrupt Mode with Falling

Pull-up * | n/a | BUTTON1
PB1 | GPIO_EXTI
1
External | Pull-up * | n/a | BUTTON2

IP | Pin | Signal | GPIO mode | GPIO pull/up pull down | Max Spee d | User Label
| | | Interrupt Mode with Falling
| PB12 | GPIO_Outp ut | Output Push Pull | No pull-up and no pull-down | Low | M_SPI_CS
| PC6 | GPIO_Input | Input mode | No pull-up and no pull-down | n/a | M_RI
| PC7 | GPIO_Outp ut | Output Push Pull | No pull-up and no pull-down | Low | M_GPIO_R3
| PA8 | GPIO_Outp ut | Output Push Pull | No pull-up and no pull-down | Low | M_GPIO_R2
| PA15 | GPIO_Outp ut | Output Push Pull | No pull-up and no pull-down | Low | M_GPIO_R1
| PB4 | GPIO_Input | Input mode | No pull-up and no pull-down | n/a | TF_DET
| PB5 | GPIO_Outp ut | Output Push Pull | No pull-up and no pull-down | Low | GPIO_2
| PB8 | GPIO_Outp ut | Output Push Pull | No pull-up and no pull-down | Low | GPIO_3
| PB9 | GPIO_Outp ut | Output Push Pull | No pull-up and no pull-down | Low | GPIO_4

# 8.2. DMA configuration

DMA request | Stream | Direction | Priority
SDIO | DMA2_Chann el4 | Memory To Peripheral | Low
USART2_RX | DMA1_Chann el6 | Peripheral To Memory | Low
USART2_TX | DMA1_Chann el7 | Memory To Peripheral | Low
USART1_RX | DMA1_Chann el5 | Peripheral To Memory | Medium *
MEMTOMEM | DMA1_Chann el1 | Memory To Memory | Low

## SDIO: DMA2_Channel4 DMA request Settings:

Mode: | Circular *
Peripheral Increment: | Disable
Memory Increment: | Enable *
Peripheral Data Width: | Word *
Memory Data Width: | Word

## USART2_RX: DMA1_Channel6 DMA request Settings:

Mode: | Normal
Peripheral Increment: | Disable
Memory Increment: | Enable *
Peripheral Data Width: | Byte
Memory Data Width: | Byte

## USART2_TX: DMA1_Channel7 DMA request Settings:

Mode: | Normal
Peripheral Increment: | Disable
Memory Increment: | Enable *
Peripheral Data Width: | Byte
Memory Data Width: | Byte

## USART1_RX: DMA1_Channel5 DMA request Settings:

Mode: | Normal
Peripheral Increment: | Disable
Memory Increment: | Enable *
Peripheral Data Width: | Byte
Memory Data Width: | Byte

## MEMTOMEM: DMA1_Channel1 DMA request Settings:

Mode: | Normal
Src Memory Increment: | Enable *
Dst Memormy Increment: | Enable *
Src Memory Data Width: | Byte
Dst Memormy Data Width: | Byte

# 8.3. NVIC configuration

Interrupt Table | Enable | Preenmption Priority | SubPriority
Non maskable interrupt | true | 0 | 0
Hard fault interrupt | true | 0 | 0
Memory management fault | true | 0 | 0
Prefetch fault, memory access fault | true | 0 | 0
Undefined instruction or illegal state | true | 0 | 0
System service call via SWI instruction | true | 0 | 0
Debug monitor | true | 0 | 0
Pendable request for system service | true | 0 | 0
System tick timer | true | 0 | 0
RTC global interrupt | true | 0 | 0
EXTI line0 interrupt | true | 3 | 0
EXTI line1 interrupt | true | 3 | 0
DMA1 channel5 global interrupt | true | 0 | 0
DMA1 channel6 global interrupt | true | 0 | 0
DMA1 channel7 global interrupt | true | 0 | 0
USB low priority or CAN RX0 interrupts | true | 0 | 0
USART2 global interrupt | true | 1 | 0
SDIO global interrupt | true | 2 | 0
DMA2 channel4 and channel5 global interrupts | true | 2 | 0
PVD interrupt through EXTI line 16 | unused
Flash global interrupt | unused
RCC global interrupt | unused
DMA1 channel1 global interrupt | unused
ADC1 and ADC2 global interrupts | unused
USB high priority or CAN TX interrupts | unused
I2C1 event interrupt | unused
I2C1 error interrupt | unused
I2C2 event interrupt | unused
I2C2 error interrupt | unused
SPI2 global interrupt | unused
USART1 global interrupt | unused

### * User modified value

# 9. Software Pack Report

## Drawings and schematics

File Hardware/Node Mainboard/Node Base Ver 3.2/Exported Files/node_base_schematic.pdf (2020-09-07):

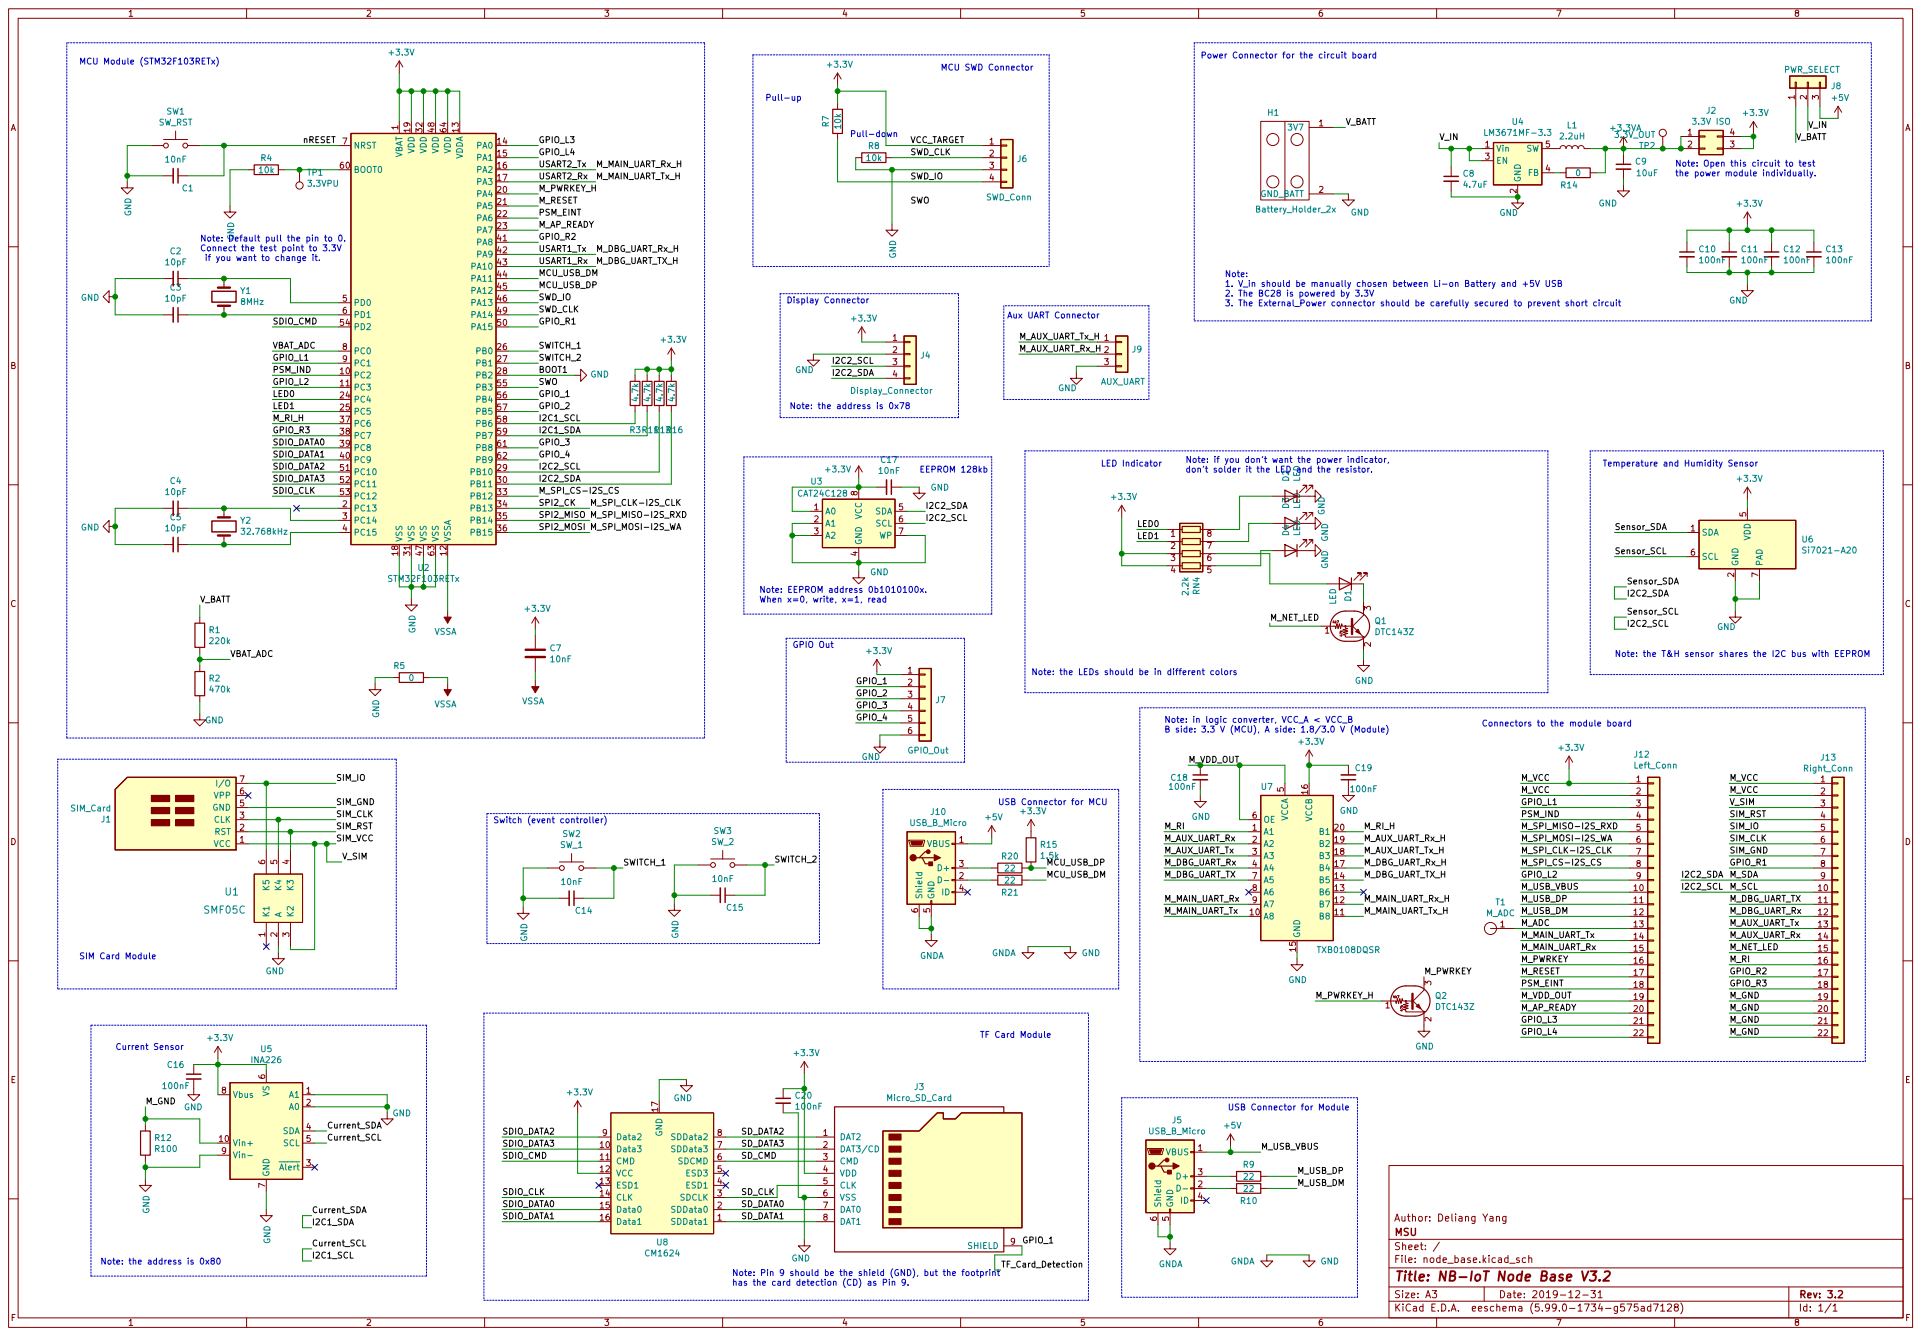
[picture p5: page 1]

the power module individually. Power Connector for the circuit board

1 VDD 19 VDD 32 VDD 48 VDD 64 VDDA 13 VSS 18 VSS 31 VSS 47 VSS 63 VSSA 12 U2 STM32F103RETx +3.3V R164.7k R34.7k R114.7k R134.7k VBUS 1 D- 2 D+ 3

Note: Open this circuit to test

Note: Default pull the pin to 0.
Connect the test point to 3.3V

if you want to change it.

Note: 1. V_in should be manually chosen between Li-on Battery and +5V USB
J9 AUX_UART GND

2. The BC28 is powered by 3.3V

Note: the address is 0x78

Note: if you dont want the power indicator, dont solder it the LED and the resistor. Note: the LEDs should be in different colors Current Sensor

Temperature and Humidity Sensor

4 SDA 5 SCL 6 WP 7 VCC

5 OE 6 A5 7 A6 8 A7 9 U7 TXB0108DQSR GND GND VSSA

Note: in logic converter, VCC_A < VCC_B
B side: 3.3 V (MCU), A side: 1.8/3.0 V (Module)

100nF VCC 1 RST 2 CLK 3 GND 5 VPP 6

Switch (event controller) Note: the address is 0x80

Id: 1/1 Title: NB-IoT Node Base V3.2

has the card detection (CD) as Pin 9.

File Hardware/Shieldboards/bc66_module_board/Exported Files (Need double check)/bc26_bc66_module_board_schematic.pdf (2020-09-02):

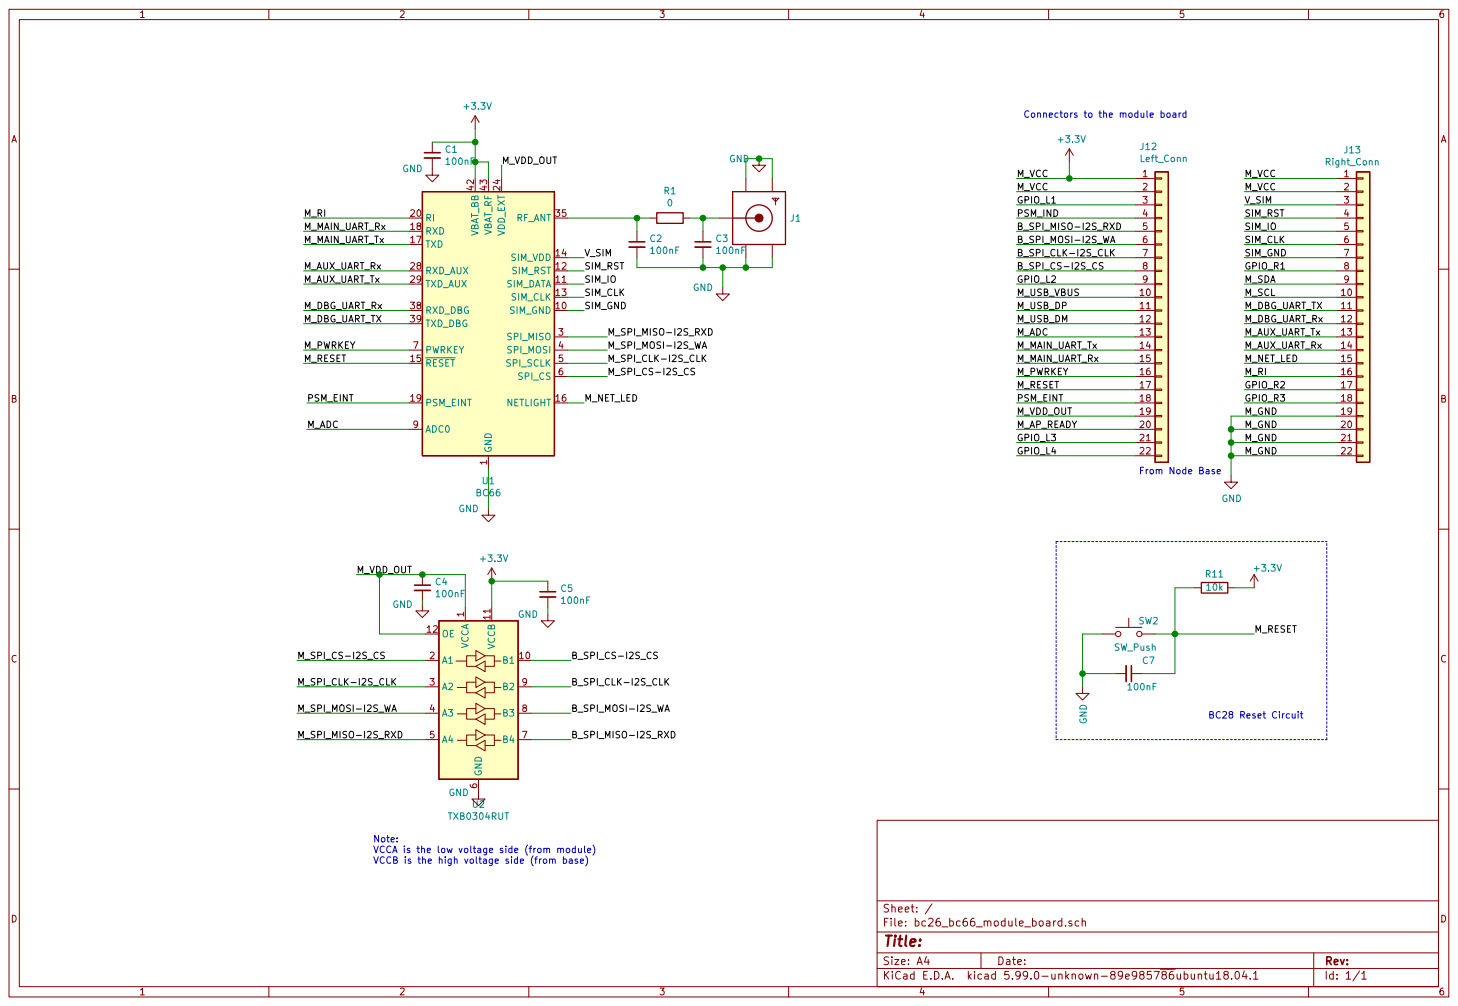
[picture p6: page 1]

1 SIM_GND 10 SIM_DATA 11 SIM_RST 12 SIM_CLK 13 SIM_VDD 14 RESET 15 NETLIGHT 16 TXD 17 RXD 18 PSM_EINT 19 RI 20 VDD_EXT 24 RXD_AUX 28 TXD_AUX 29 SPI_MISO 3 RF_ANT 35 RXD_DBG 38 TXD_DBG 39 SPI_MOSI 4 VBAT_BB 42 VBAT_RF 43 SPI_SCLK 5 SPI_CS 6 PWRKEY 7 ADC0 9 U1 BC66

6 B4 7 B3 8 B2 9 U2 TXB0304RUT M_VDD_OUT Note: VCCA is the low voltage side (from module)

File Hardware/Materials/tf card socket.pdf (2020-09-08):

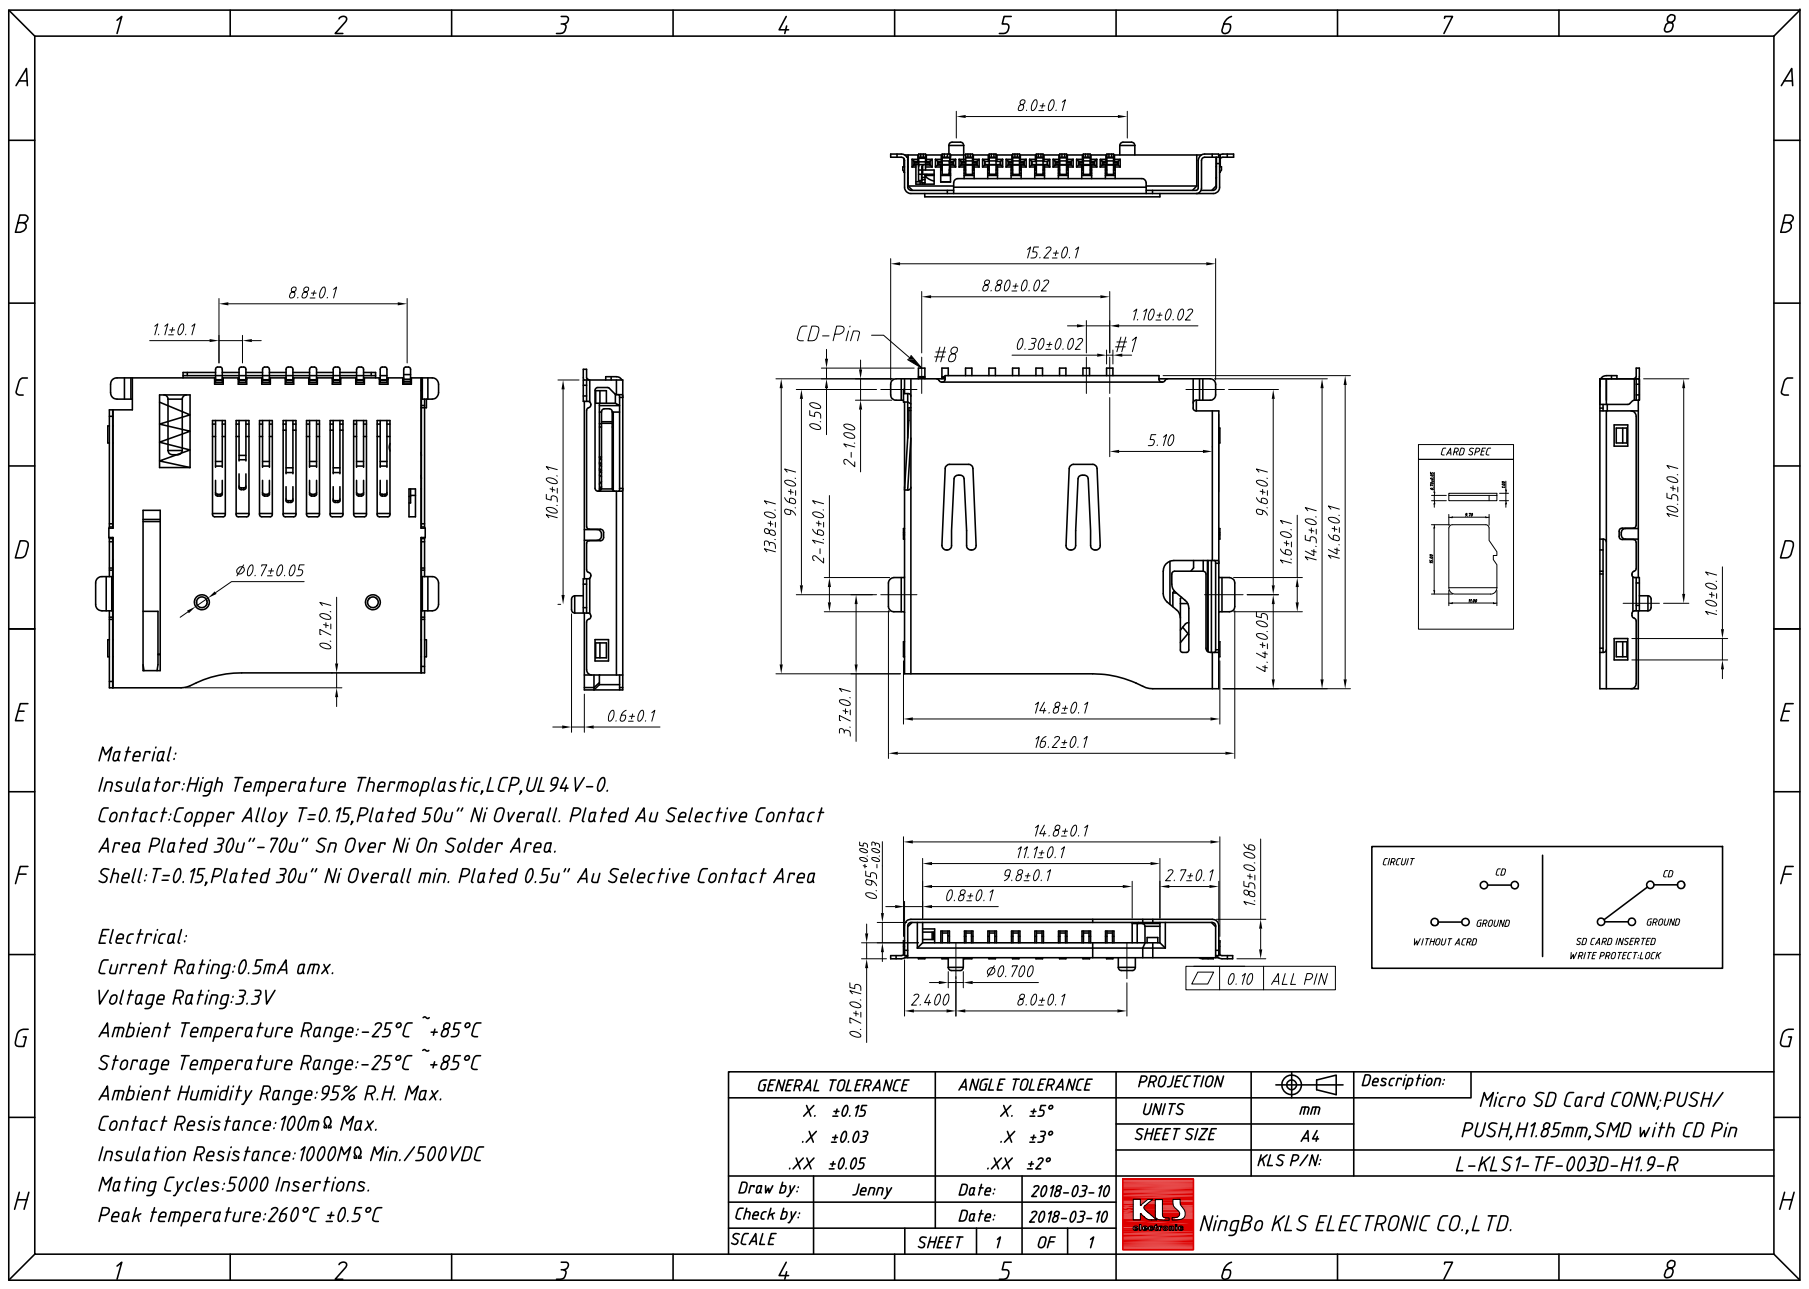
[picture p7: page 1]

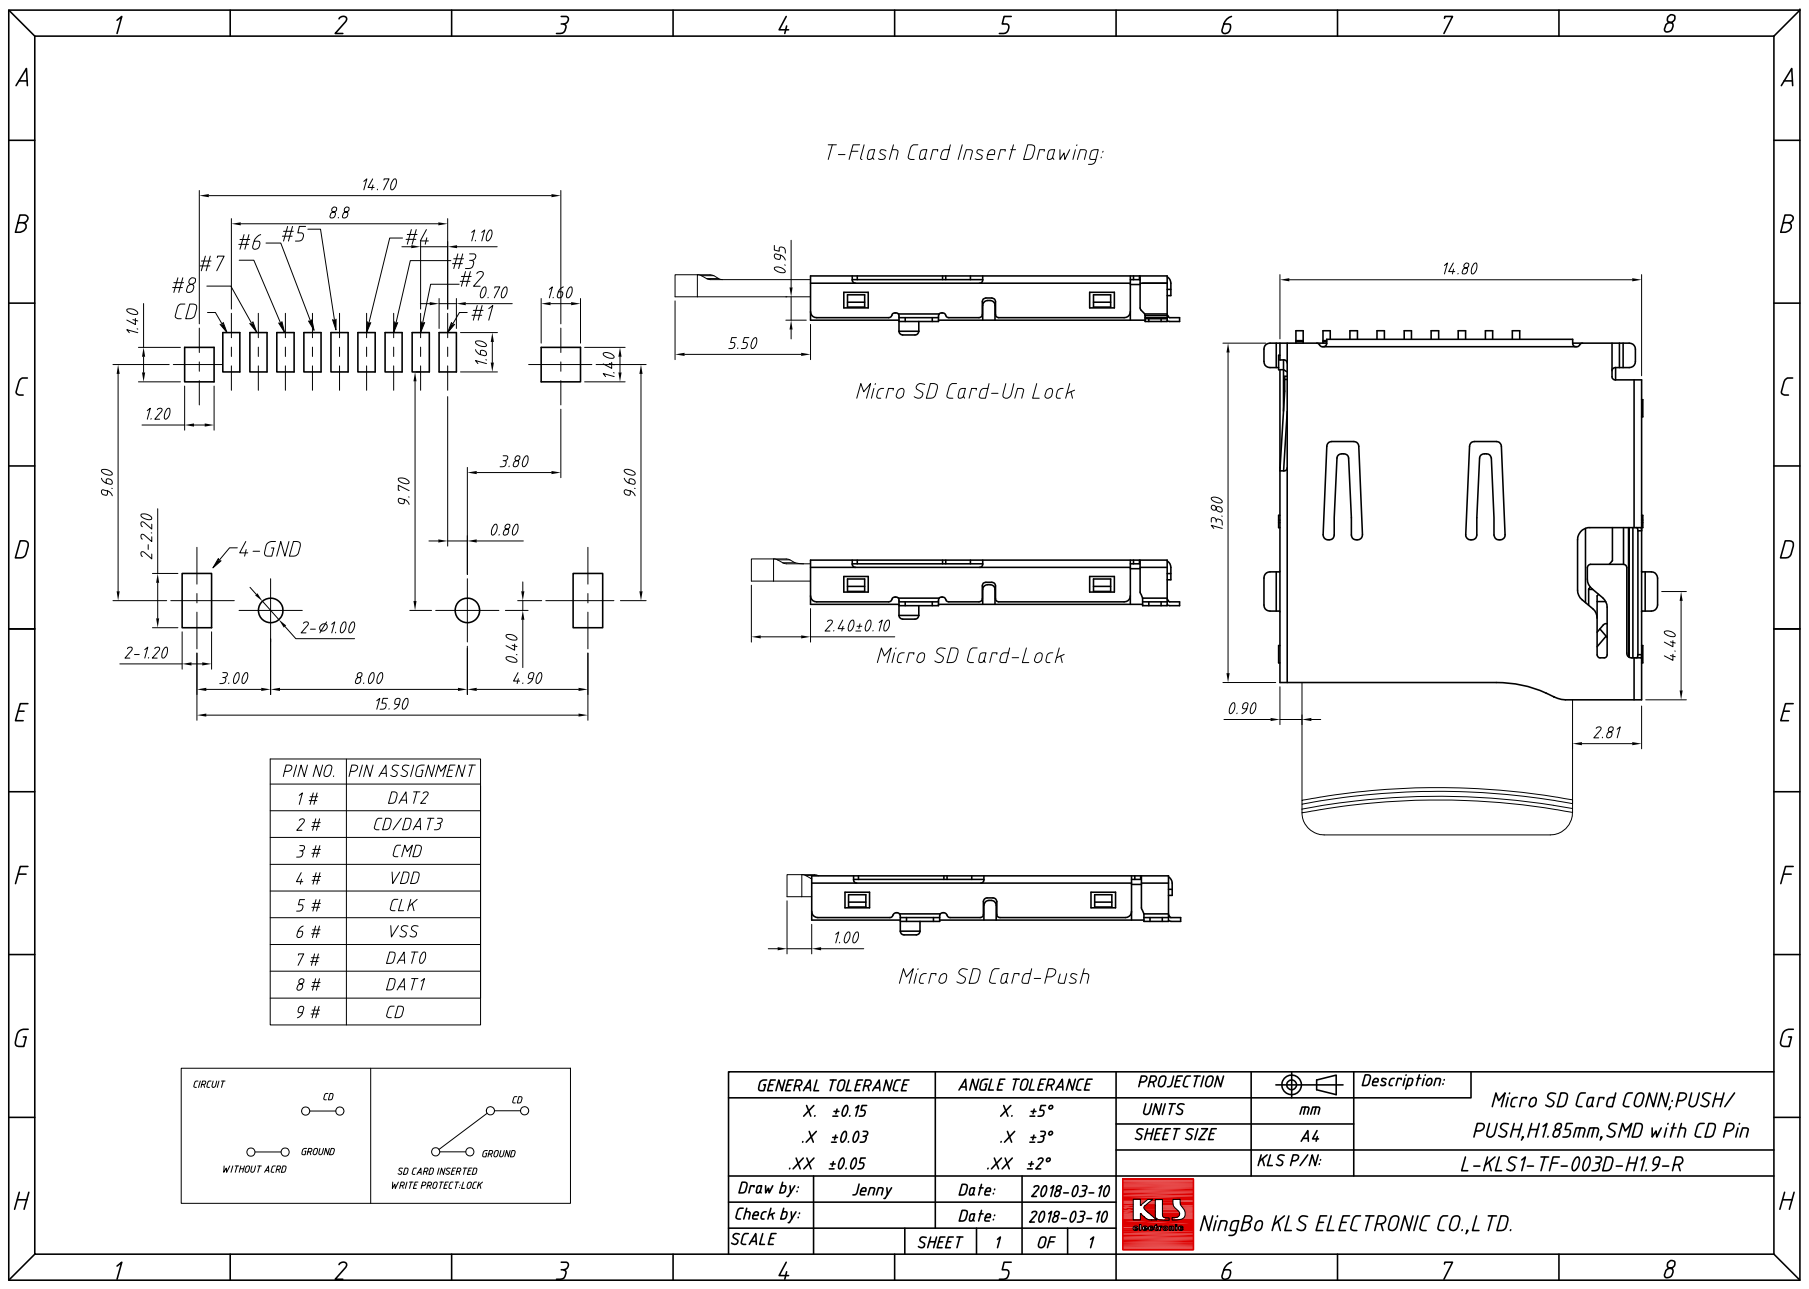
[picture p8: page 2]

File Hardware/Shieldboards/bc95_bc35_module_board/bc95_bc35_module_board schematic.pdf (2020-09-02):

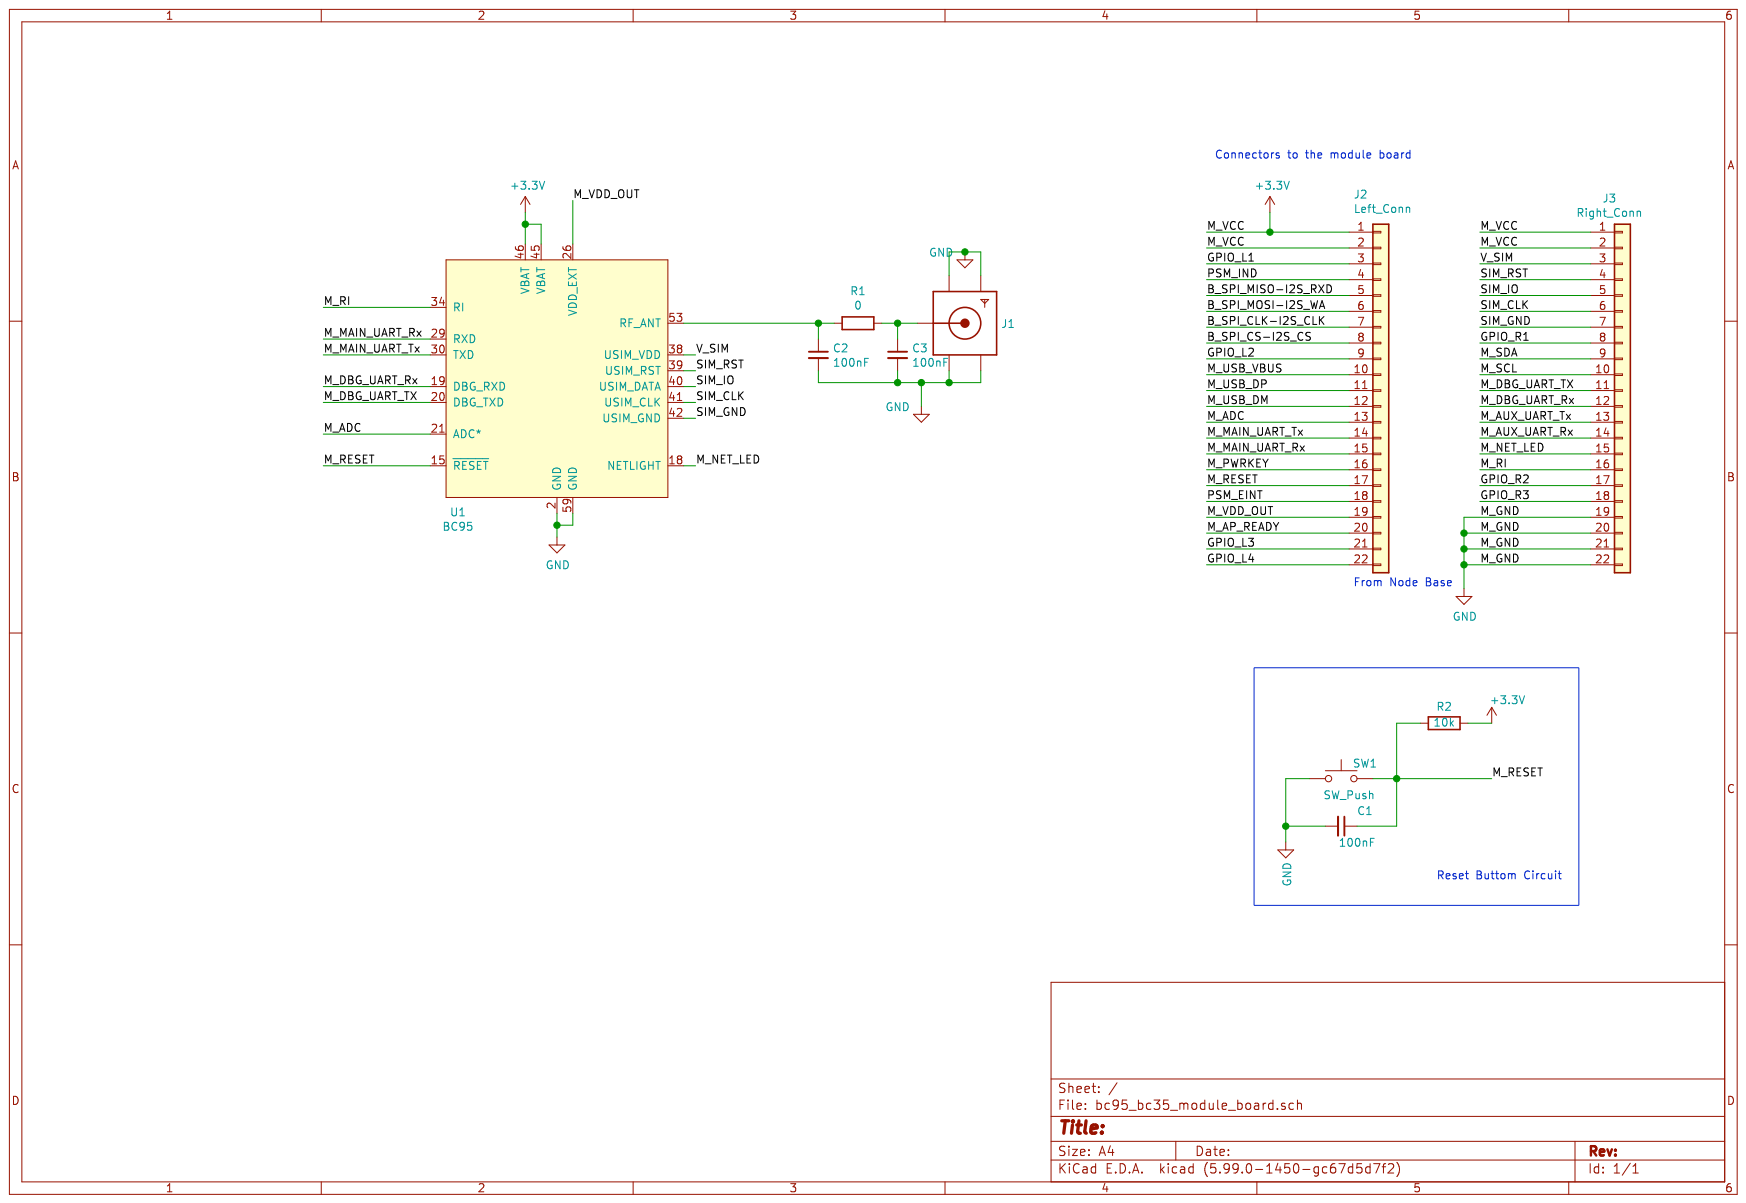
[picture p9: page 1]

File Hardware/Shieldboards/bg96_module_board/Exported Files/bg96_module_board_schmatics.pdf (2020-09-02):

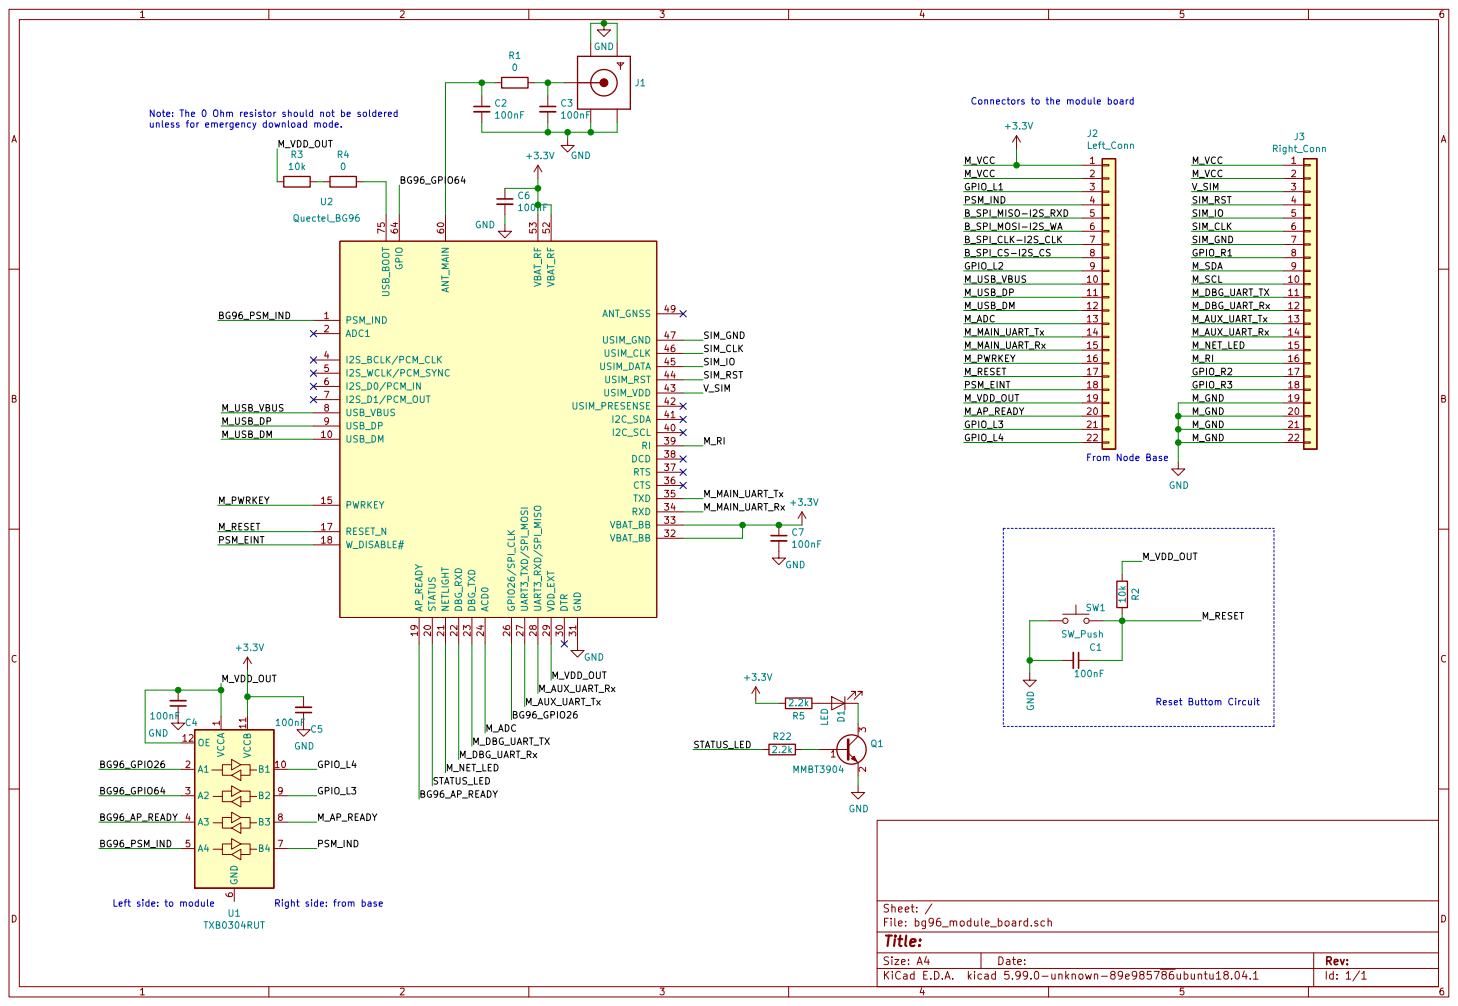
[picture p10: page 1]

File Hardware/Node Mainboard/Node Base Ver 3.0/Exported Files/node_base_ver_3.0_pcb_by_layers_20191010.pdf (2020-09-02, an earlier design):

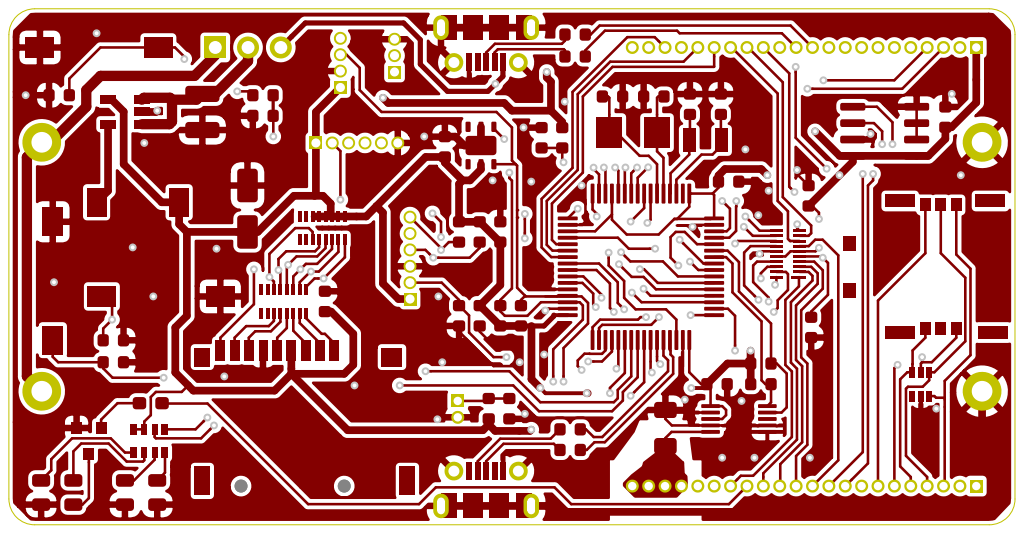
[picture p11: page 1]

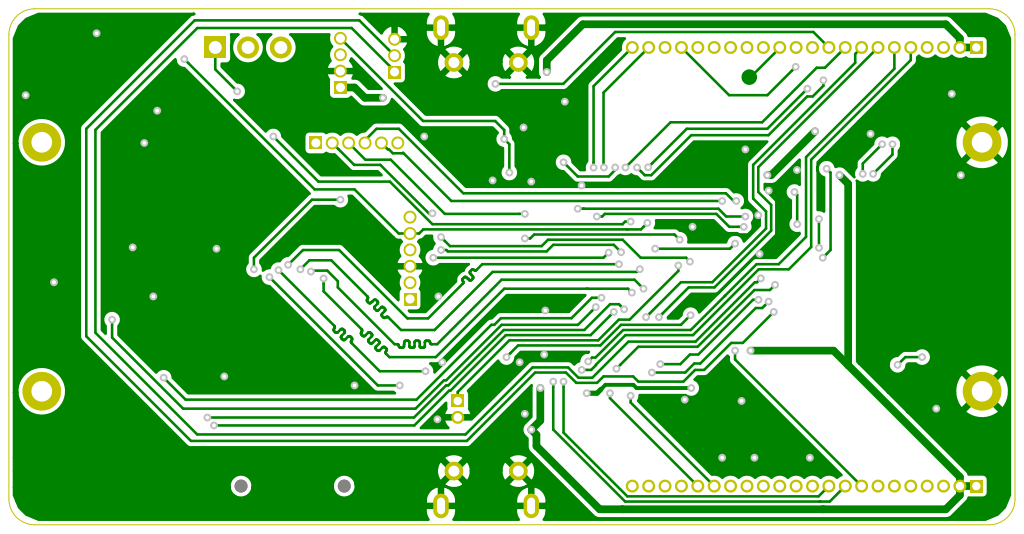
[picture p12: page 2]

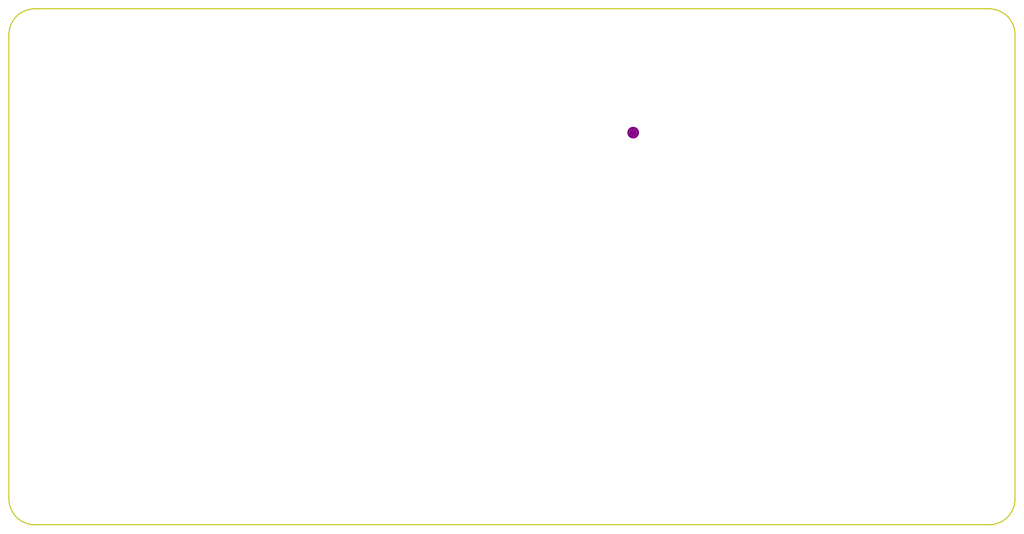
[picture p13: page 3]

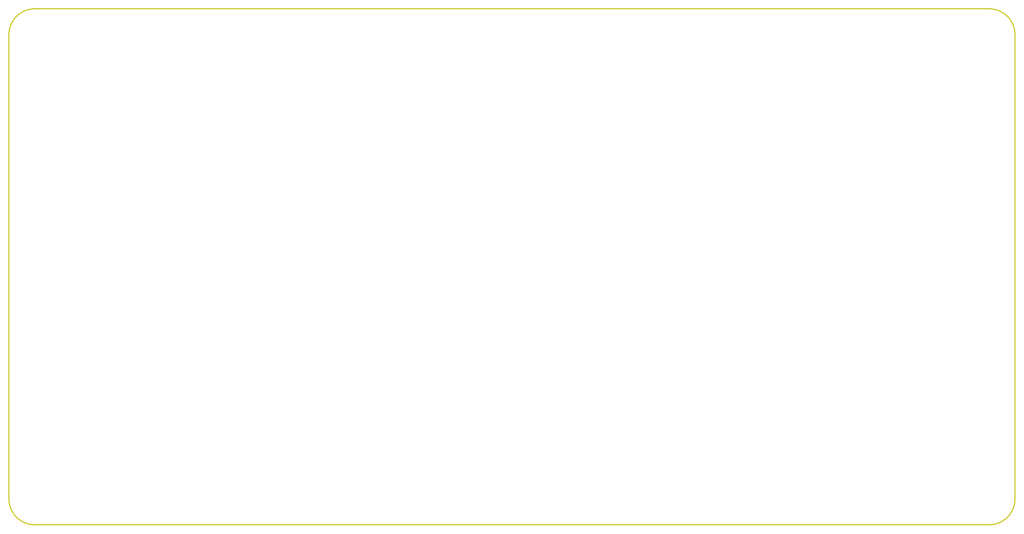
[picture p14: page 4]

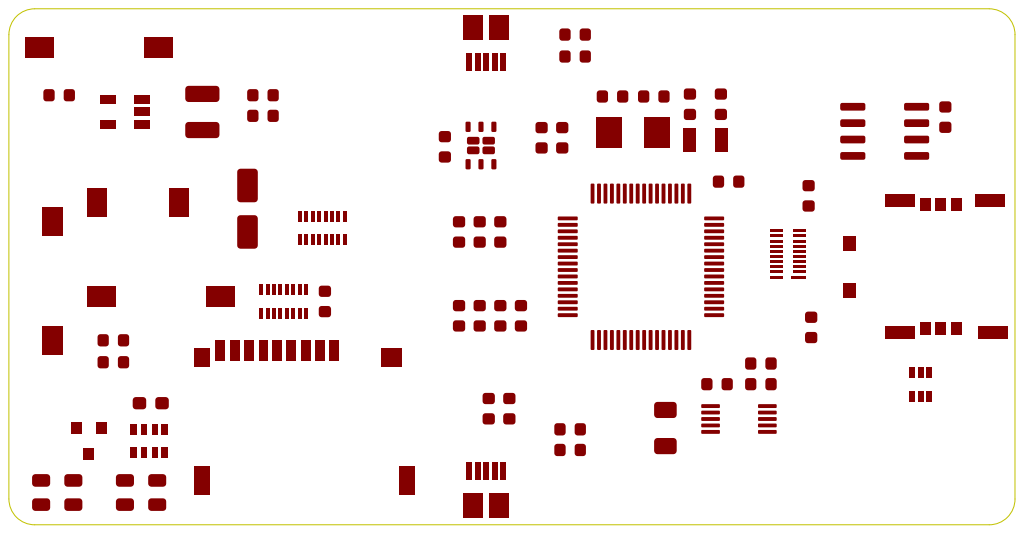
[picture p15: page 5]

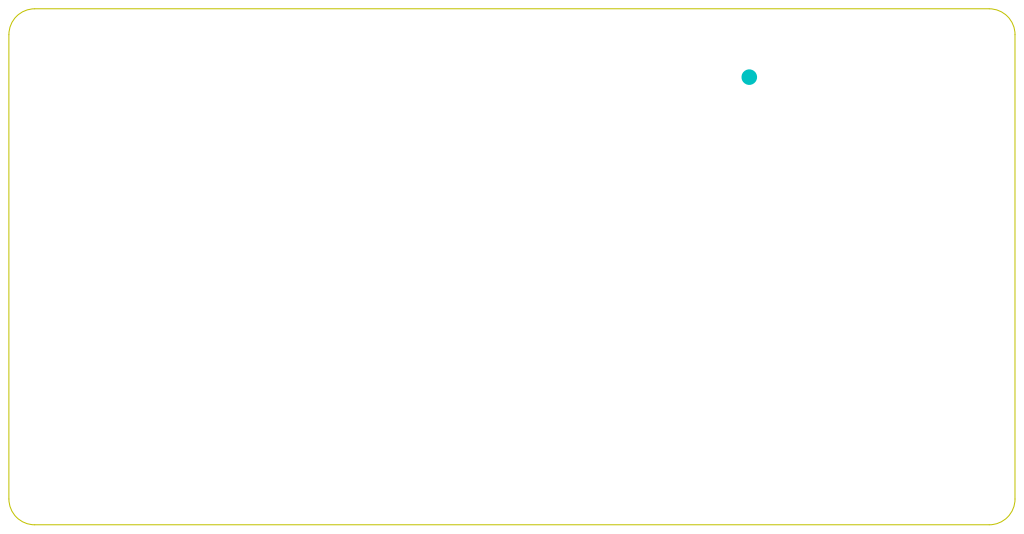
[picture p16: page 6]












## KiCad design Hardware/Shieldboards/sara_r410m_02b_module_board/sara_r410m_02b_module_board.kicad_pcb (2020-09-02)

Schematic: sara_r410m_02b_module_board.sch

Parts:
C1, C2, C3, C4, C5, C6, C7, C8: 100nF; C_0603_1608Metric
D1: LED; LED_0805_2012Metric
J1: 1865; SMA_Antenna
J2: Left_Conn; PinHeader_1x22_P1.27mm_Vertical
J3: Right_Conn; PinHeader_1x22_P1.27mm_Vertical
J4: USB_DET_Conn; PinHeader_1x02_P1.27mm_Vertical
Q1, Q2: MMBT3904; SOT-23
R1: 0; R_0603_1608Metric
R2: 4.7k; R_0603_1608Metric
R3: 47k; R_0603_1608Metric
R5, R22: 2.2k; R_0603_1608Metric
SW1: SW_Push; SMD_Switch
T1: M_PWR_KEY; test_pad
U1: uBlox_SARA-R410M-02B; Ublox_SARA-R410M-02B
U2, U3: TXB0304RUT; Texas_R_PUQFN-N12

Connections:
/B_SPI_CLK-I2S_CLK: J2.7
/B_SPI_CS-I2S_CS: J2.8
/B_SPI_MISO-I2S_RXD: J2.5
/B_SPI_MOSI-I2S_WA: J2.6
/GPIO_L1: J2.3, U2.7
/GPIO_L2: J2.9, U2.8
/GPIO_L3: J2.21, U2.9
/GPIO_L4: J2.22, R2.2
/GPIO_R1: J3.8, U3.10
/GPIO_R2: J3.17
/GPIO_R3: J3.18
/M_ADC: J2.13
/M_AP_READY: J2.20
/M_AUX_UART_Rx: J3.14
/M_AUX_UART_Tx: J3.13
/M_DBG_UART_Rx: J3.12
/M_DBG_UART_TX: J3.11
/M_MAIN_UART_Rx: J2.15, U1.12 (TXD)
/M_MAIN_UART_Tx: J2.14, U1.13 (RXD)
/M_NET_LED: J3.15, U1.16 (GPIO1)
/M_PWRKEY: J2.16
/M_PWR_KEY_NEW: Q2.3, T1.1, U1.15 (PWR_ON)
/M_RESET: J2.17, U2.10
/M_RI: J3.16, U1.7 (RI)
/M_SCL: J3.10, U3.8
/M_SDA: J3.9, U3.9
/M_USB_DM: J2.12, U1.28 (USB_D-)
/M_USB_DP: J2.11, U1.29 (USB_D+)
/M_USB_VBUS: J2.10, J4.1
/M_VDD_OUT: C4.2, C7.2, J2.19, U1.4 (V_INT), U2.1, U2.12, U3.1, U3.12
/PSM_EINT: J2.18
/PSM_IND: J2.4
/SARA_GPIO2: U1.23 (GPIO2), U2.4
/SARA_GPIO3: U1.24 (GPIO3), U2.3
/SARA_GPIO5: U1.42 (GPIO5), U3.2
/SARA_GPIO6: U1.19 (GPIO6), U2.5
/SARA_RESET: C1.1, SW1.2, U1.18 (RESET_N), U2.2
/SARA_SCL: U1.27 (SCL), U3.4
/SARA_SDA: U1.26 (SDA), U3.3
/SARA_STATUS_LED: R22.2, U1.25 (GPIO4)
/SIM_CLK: J3.6, U1.38 (SIM_CLK)
/SIM_IO: J3.5, U1.39 (SIM_IO)
/SIM_RST: J3.4, U1.40 (SIM_RST)
/V_SIM: J3.3, U1.41 (VSIM)
GND: C1.2, C2.2, C3.2, C4.1, C5.1, C6.2, C7.1, C8.1, J1.GND1, J1.GND2, J1.GND3, J1.GND4, J3.7, J3.19, J3.20, J3.21, J3.22, Q1.2, Q2.2, R3.1, SW1.1, U1.1 (GND), U1.3 (GND), U1.5 (GND), U1.14 (GND), U1.20 (GND), U1.21 (GND), U1.22 (GND), U1.30 (GND), U1.32 (GND), U1.43 (GND), U1.50 (GND), U1.54 (GND), U1.55 (GND), U1.57 (GND), U1.58 (GND), U1.59 (GND), U1.60 (GND), U1.61 (GND), U1.63 (GND), U1.64 (GND), U1.65 (GND), U1.66 (GND), U1.67 (GND), U1.68 (GND), U1.69 (GND), U1.70 (GND), U1.71 (GND), U1.72 (GND), U1.73 (GND), U1.74 (GND), U1.75 (GND), U1.76 (GND), U1.77 (GND), U1.78 (GND), U1.79 (GND), U1.80 (GND), U1.81 (GND), U1.82 (GND), U1.83 (GND), U1.84 (GND), U1.85 (GND), U1.86 (GND), U1.87 (GND), U1.88 (GND), U1.89 (GND), U1.90 (GND), U1.91 (GND), U1.92 (GND), U1.93 (GND), U1.94 (GND), U1.95 (GND), U1.96 (GND), U2.6, U3.6
unnamed: C2.1, R1.2, U1.56 (ANT)
unnamed: C3.1, J1.P, R1.1
unnamed: D1.1 (K), Q1.3
unnamed: D1.2 (A), R5.2
unnamed: J4.2, U1.17 (VUSB_DET)
unnamed: Q1.1, R22.1
unnamed: Q2.1, R2.1, R3.2

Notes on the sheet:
Connectors to the module board
From Node Base
Reset Buttom Circuit
For right hand part
For left hand part
Note: no pull-up resistor needed (has internal one)
Note: The SARA uses the STUPID ITU-T V.24 recommendation. So the "RXD" on the module means the RXD of the MCU. It actually outputs data.

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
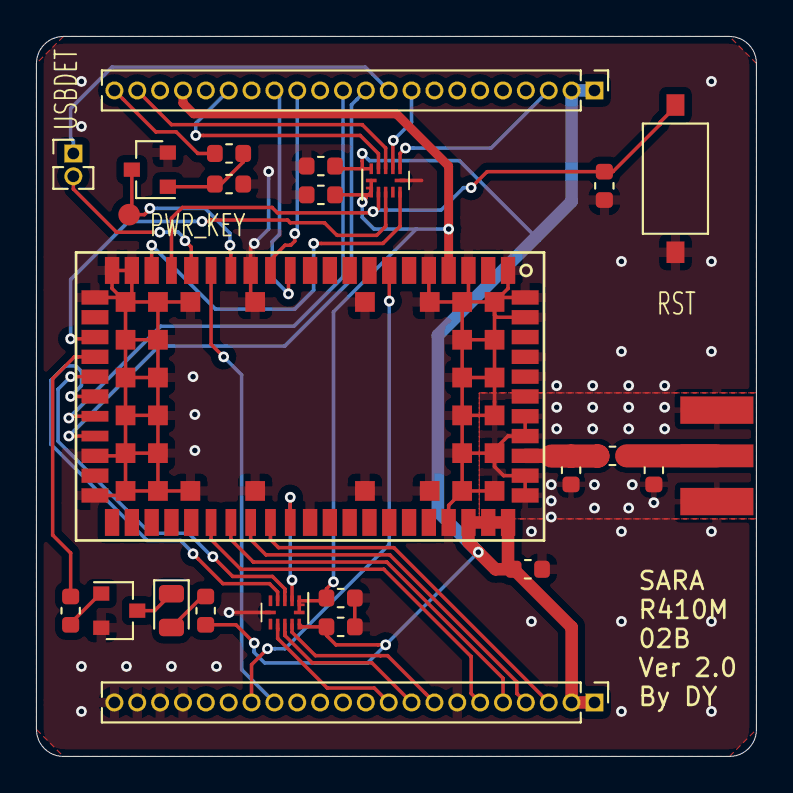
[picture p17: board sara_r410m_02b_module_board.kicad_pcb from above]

Board: 2 copper layers, 40.0 x 40.0 mm, 25 parts (0 on the bottom side), 38 nets.

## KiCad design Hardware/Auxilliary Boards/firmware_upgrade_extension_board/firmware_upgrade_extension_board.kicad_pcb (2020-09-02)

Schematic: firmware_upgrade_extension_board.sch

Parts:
J1: MAIN_UART_CONN; PinHeader_1x04_P2.54mm_Vertical
J2: Left_Conn; PinSocket_1x22_P1.27mm_Vertical
J3: Right_Conn; PinSocket_1x22_P1.27mm_Vertical
J4: PWR_KEY_TO_GND_CONN; PinHeader_1x02_P2.54mm_Vertical
J5: VCC_CONN; PinHeader_1x03_P2.54mm_Vertical
J6: GND_CONN; PinHeader_1x03_P2.54mm_Vertical
J7: DBG_UART_CONN; PinHeader_1x05_P2.54mm_Vertical
J8: USB_CONN; PinHeader_1x04_P2.54mm_Vertical
SW1: PWR_KEY_TO_GND_BTN; SMD_Switch

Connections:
+3V3: J2.1, J2.2, J3.1, J3.2, J5.1, J5.2, J5.3
/B_SPI_CLK-I2S_CLK: J2.7
/B_SPI_CS-I2S_CS: J2.8
/B_SPI_MISO-I2S_RXD: J2.5
/B_SPI_MOSI-I2S_WA: J2.6
/GPIO_L1: J2.3
/GPIO_L2: J2.9
/GPIO_L3: J2.21
/GPIO_L4: J2.22
/GPIO_R1: J3.8
/GPIO_R2: J3.17
/GPIO_R3: J3.18
/M_ADC: J2.13
/M_AP_READY: J2.20
/M_AUX_UART_Rx: J3.14, J7.2
/M_AUX_UART_Tx: J3.13, J7.3
/M_DBG_UART_Rx: J3.12, J7.4
/M_DBG_UART_TX: J3.11, J7.5
/M_MAIN_UART_Rx: J1.1, J2.15
/M_MAIN_UART_Tx: J1.2, J2.14
/M_NET_LED: J3.15
/M_PWRKEY: J2.16, J4.2, SW1.2
/M_RESET: J2.17
/M_RI: J3.16
/M_SCL: J3.10
/M_SDA: J3.9
/M_USB_DM: J2.12, J8.2
/M_USB_DP: J2.11, J8.3
/M_USB_VBUS: J2.10, J8.4
/M_VDD_OUT: J2.19
/PSM_EINT: J2.18
/PSM_IND: J2.4
/SIM_CLK: J3.6
/SIM_GND: J3.7
/SIM_IO: J3.5
/SIM_RST: J3.4
/V_SIM: J3.3
GND: J1.3, J3.19, J3.20, J3.21, J3.22, J4.1, J6.1, J6.2, J6.3, J7.1, J8.1, SW1.1

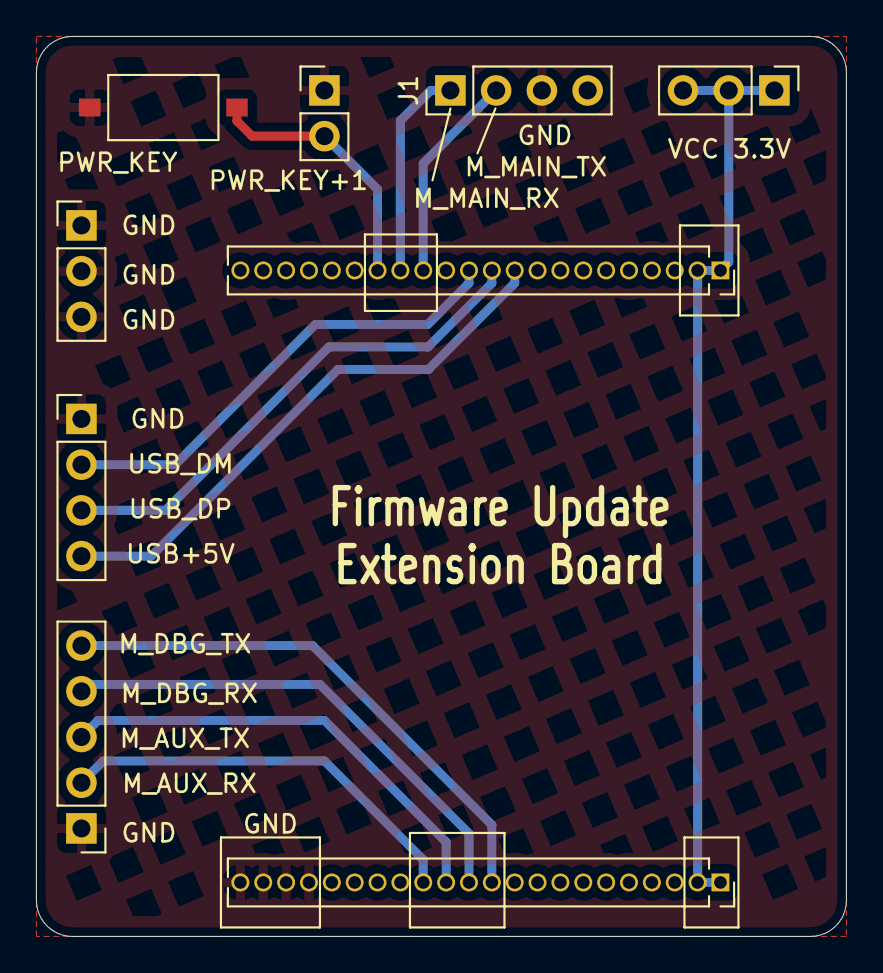
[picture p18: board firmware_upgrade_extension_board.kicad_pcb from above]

Board: 2 copper layers, 45.0 x 50.0 mm, 9 parts (0 on the bottom side), 12 nets.

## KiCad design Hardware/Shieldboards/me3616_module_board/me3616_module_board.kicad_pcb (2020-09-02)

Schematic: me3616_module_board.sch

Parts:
C1, C2, C3, C7: 100nF; C_0603_1608Metric
J1: 1865; SMA_Antenna
J2: USB_V_BUS_EN; PinHeader_1x02_P1.27mm_Vertical
J12: Left_Conn; PinHeader_1x22_P1.27mm_Vertical
J13: Right_Conn; PinHeader_1x22_P1.27mm_Vertical
Q1, Q2: MMBT3904; SOT-23
R1: 0; R_0603_1608Metric
R2, R4: 4.7k; R_0603_1608Metric
R3, R5: 47k; R_0603_1608Metric
SW2: SW_Push; SMD_Switch
T2: ME3616_MAIN_RXD; test_pad
T3: ME3616_DBG_RXD; test_pad
T4: ME3616_MAIN_TXD; test_pad
T5: ME3616_DBG_TXD; test_pad
U1: ME3616; ZTE_ME3616

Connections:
+3V3: C1.1, J2.2, J12.1, J12.2, J13.1, J13.2, U1.31 (VCC_BB), U1.32 (VCC_RF)
/B_SPI_CLK-I2S_CLK: J12.7
/B_SPI_CS-I2S_CS: J12.8
/B_SPI_MISO-I2S_RXD: J12.5
/B_SPI_MOSI-I2S_WA: J12.6
/GPIO_L1: J12.3, U1.34 (GPIO1)
/GPIO_L2: J12.9, U1.35 (GPIO2)
/GPIO_L3: J12.21
/GPIO_L4: J12.22, R2.2
/GPIO_R1: J13.8
/GPIO_R2: J13.17
/GPIO_R3: J13.18
/ME3616_POWER_ON: Q2.3, U1.19 (POWER_ON)
/ME3616_RESET: Q1.3, U1.17 (RESET)
/M_ADC: J12.13
/M_AP_READY: J12.20
/M_AUX_UART_RX: J13.14
/M_AUX_UART_TX: J13.13
/M_DBG_UART_RX: J13.12, T3.1, U1.2 (UART_DEBUG_RXD)
/M_DBG_UART_TX: J13.11, T5.1, U1.1 (UART_BEBUG_TXD)
/M_MAIN_UART_RX: J12.15, T2.1, U1.10 (UART1_RXD)
/M_MAIN_UART_TX: J12.14, T4.1, U1.9 (UART1_TXD)
/M_NET_LED: J13.15, U1.21 (SYS_STATE)
/M_PWRKEY: J12.16
/M_RESET: C7.1, J12.17, R4.2, SW2.2
/M_RI: J13.16
/M_SCL: J13.10
/M_SDA: J13.9
/M_USB_DM: J12.12, U1.39 (USB_DM)
/M_USB_DP: J12.11, U1.40 (USB_DP)
/M_USB_VBUS: J12.10
/M_VDD_OUT: J12.19, U1.20 (VCC1V8_OUT)
/PSM_EINT: J12.18, U1.18 (WAKEUP_IN)
/PSM_IND: J12.4
/SIM_CLK: J13.6, U1.13 (USIM_CLK)
/SIM_IO: J13.5, U1.14 (USIM_DATA)
/SIM_RST: J13.4, U1.12 (USIM_RESET)
/V_SIM: J13.3, U1.15 (USIM_VCC)
GND: C1.2, C2.2, C3.2, C7.2, J1.GND1, J1.GND2, J1.GND3, J1.GND4, J13.7, J13.19, J13.20, J13.21, J13.22, Q1.2, Q2.2, R3.1, R5.1, SW2.1, U1.22 (GND), U1.23 (GND), U1.25 (GND), U1.26 (GND), U1.28 (GND), U1.29 (GND), U1.30 (GND)
unnamed: C2.1, R1.2, U1.27 (MAIN_ANT)
unnamed: C3.1, J1.P, R1.1
unnamed: J2.1, U1.33 (VBUS_3V3)
unnamed: Q1.1, R4.1, R5.2
unnamed: Q2.1, R2.1, R3.2

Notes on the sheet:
Note: The ME3616 uses the LED on the base board.
Connectors to the module board
From Node Base
ME3616 Onboard Reset Circuit (No pull-up needed, but add one if this circuit doesn't work)

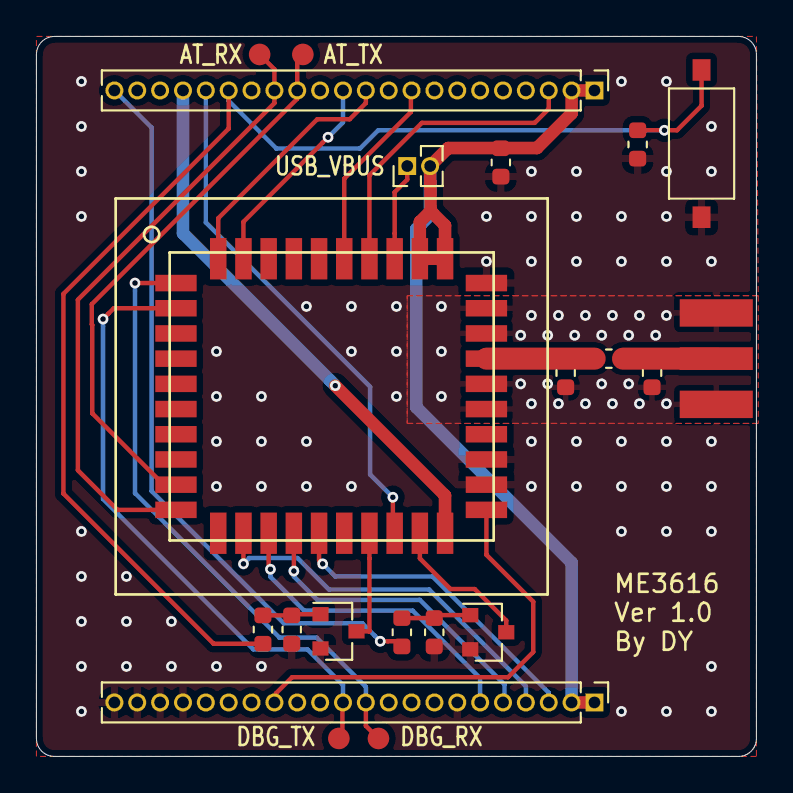
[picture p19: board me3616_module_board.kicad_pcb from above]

Board: 2 copper layers, 40.0 x 40.0 mm, 21 parts (0 on the bottom side), 26 nets.

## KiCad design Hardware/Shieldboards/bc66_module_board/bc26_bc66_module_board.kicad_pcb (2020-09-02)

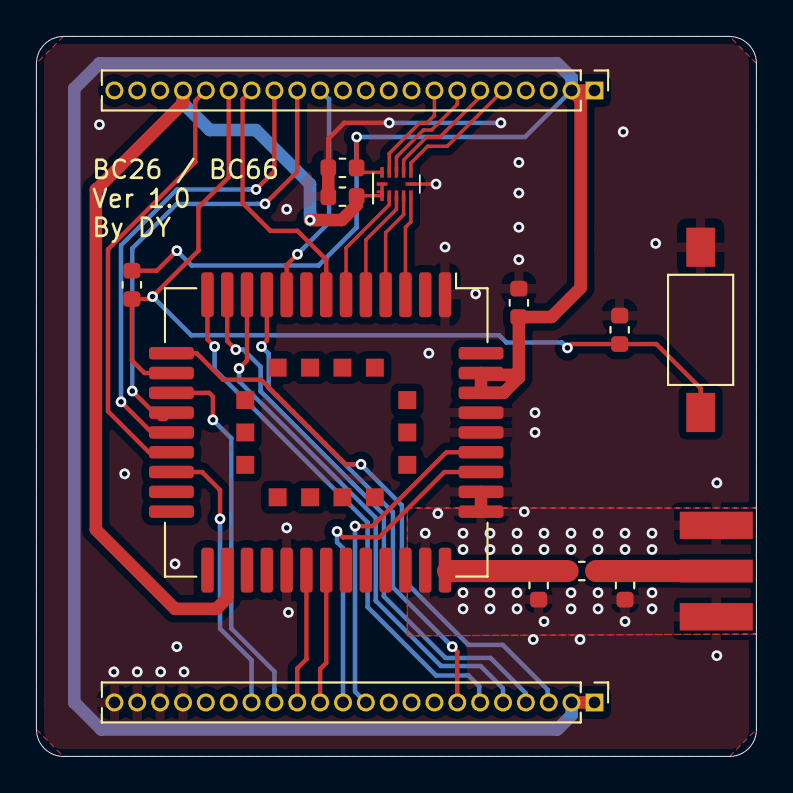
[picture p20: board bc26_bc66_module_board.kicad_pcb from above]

Board: 2 copper layers, 40.0 x 40.0 mm, 14 parts (0 on the bottom side), 30 nets.

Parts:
C1, C2, C3, C4, C5, C7: 100nF; C_0603_1608Metric
J1: 1865; SMA_Antenna
J12: Left_Conn; PinHeader_1x22_P1.27mm_Vertical
J13: Right_Conn; PinHeader_1x22_P1.27mm_Vertical
R1: 0; R_0603_1608Metric
R11: 10k; R_0603_1608Metric
SW2: SW_Push; SW_SPST_FSMSM
U1: BC66; Quectel_BC66
U2: TXB0304RUT; Texas_R_PUQFN-N12

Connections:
+3V3: C1.1, C5.1, J12.1, J12.2, J13.1, J13.2, R11.2, U1.42, U1.43, U2.11
/B_SPI_CLK-I2S_CLK: J12.7, U2.9
/B_SPI_CS-I2S_CS: J12.8, U2.10
/B_SPI_MISO-I2S_RXD: J12.5, U2.7
/B_SPI_MOSI-I2S_WA: J12.6, U2.8
/M_ADC: J12.13, U1.9
/M_AUX_UART_Rx: J13.14, U1.28
/M_AUX_UART_Tx: J13.13, U1.29
/M_DBG_UART_Rx: J13.12, U1.38
/M_DBG_UART_TX: J13.11, U1.39
/M_MAIN_UART_Rx: J12.15, U1.18
/M_MAIN_UART_Tx: J12.14, U1.17
/M_NET_LED: J13.15, U1.16
/M_PWRKEY: J12.16, U1.7
/M_RESET: C7.1, J12.17, R11.1, SW2.2, U1.15
/M_RI: J13.16, U1.20
/M_SPI_CLK-I2S_CLK: U1.5, U2.3
/M_SPI_CS-I2S_CS: U1.6, U2.2
/M_SPI_MISO-I2S_RXD: U1.3, U2.5
/M_SPI_MOSI-I2S_WA: U1.4, U2.4
/M_VDD_OUT: C4.1, J12.19, U1.24, U2.1, U2.12
/PSM_EINT: J12.18, U1.19
/SIM_CLK: J13.6, U1.13
/SIM_GND: J13.7, U1.10
/SIM_IO: J13.5, U1.11
/SIM_RST: J13.4, U1.12
/V_SIM: J13.3, U1.14
GND: C1.2, C2.2, C3.2, C4.2, C5.2, C7.2, J1.GND1, J1.GND2, J1.GND3, J1.GND4, J13.19, J13.20, J13.21, J13.22, SW2.1, U1.1, U1.27, U1.34, U1.36, U1.37, U1.40, U1.41, U2.6
unnamed: C2.1, R1.2, U1.35
unnamed: C3.1, J1.P, R1.1

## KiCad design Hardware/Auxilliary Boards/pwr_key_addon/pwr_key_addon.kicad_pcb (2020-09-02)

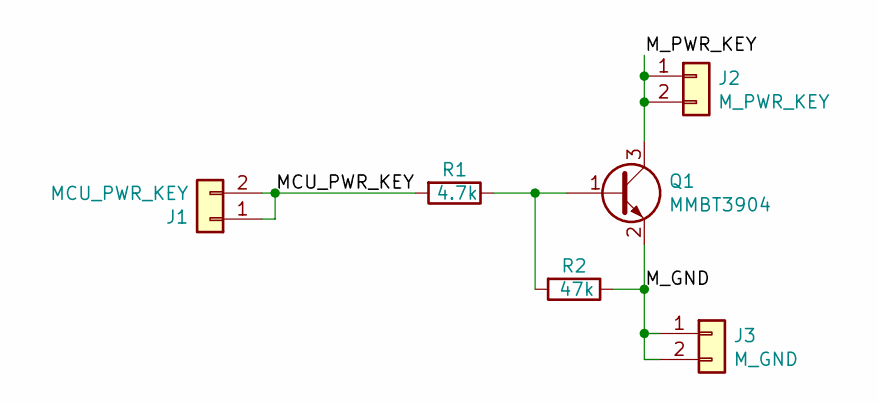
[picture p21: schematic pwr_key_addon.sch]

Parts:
J1: MCU_PWR_KEY; PinHeader_1x02_P1.27mm_Vertical
J2: M_PWR_KEY; PinHeader_1x02_P1.27mm_Vertical
J3: M_GND; PinHeader_1x02_P1.27mm_Vertical
Q1: MMBT3904; SOT-23
R1: 4.7k; R_0805_2012Metric
R2: 47k; R_0805_2012Metric

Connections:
/MCU_PWR_KEY: J1.1, J1.2, R1.2
/M_GND: J3.1, J3.2, Q1.2 (E), R2.1
/M_PWR_KEY: J2.1, J2.2, Q1.3 (C)
unnamed: Q1.1 (B), R1.1, R2.2

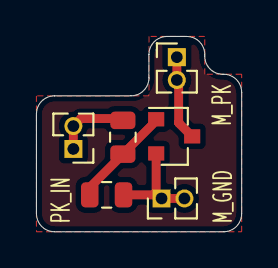
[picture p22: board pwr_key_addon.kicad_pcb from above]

Board: 2 copper layers, 11.4 x 10.8 mm, 6 parts (0 on the bottom side), 4 nets.

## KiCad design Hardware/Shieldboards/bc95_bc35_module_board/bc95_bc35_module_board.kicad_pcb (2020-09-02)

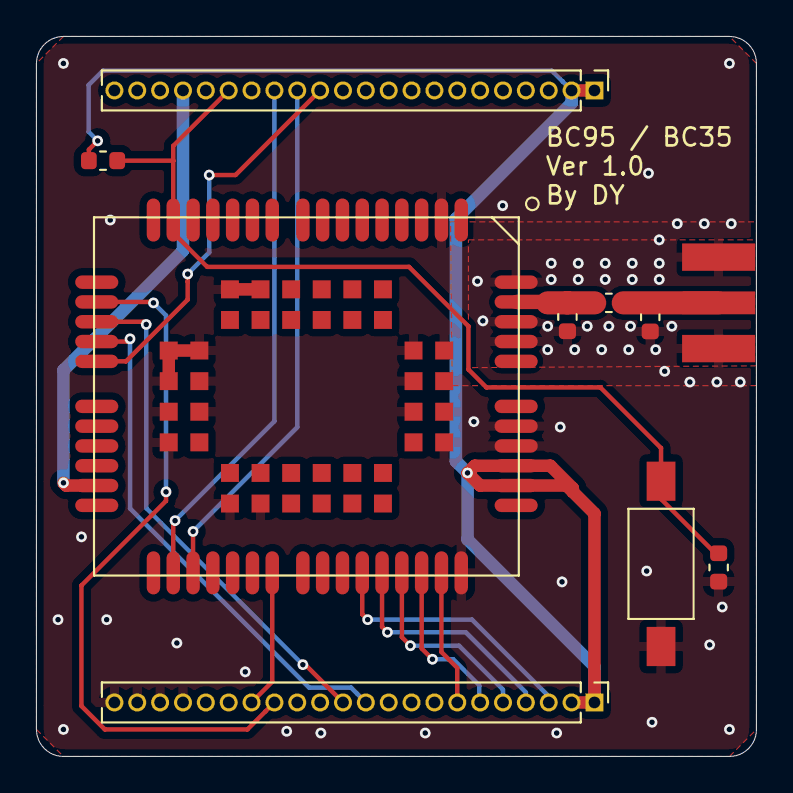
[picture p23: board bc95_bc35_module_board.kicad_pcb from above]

Board: 2 copper layers, 40.0 x 40.0 mm, 10 parts (0 on the bottom side), 18 nets.

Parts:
C1, C2, C3: 100nF; C_0603_1608Metric
J1: 1865; SMA_Antenna
J2: Left_Conn; PinHeader_1x22_P1.27mm_Vertical
J3: Right_Conn; PinHeader_1x22_P1.27mm_Vertical
R1: 0; R_0603_1608Metric
R2: 10k; R_0603_1608Metric
SW1: SW_Push; SW_SPST_FSMSM
U1: BC95; Quectel_BC95_BC35

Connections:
+3V3: J2.1, J2.2, J3.1, J3.2, R2.2, U1.45, U1.46
/M_ADC: J2.13, U1.21
/M_DBG_UART_Rx: J3.12, U1.19
/M_DBG_UART_TX: J3.11, U1.20
/M_MAIN_UART_Rx: J2.15, U1.29
/M_MAIN_UART_Tx: J2.14, U1.30
/M_NET_LED: J3.15, U1.18
/M_RESET: C1.1, J2.17, R2.1, SW1.2, U1.15
/M_RI: J3.16, U1.34
/M_VDD_OUT: J2.19, U1.26
/SIM_CLK: J3.6, U1.41
/SIM_GND: J3.7, U1.42
/SIM_IO: J3.5, U1.40
/SIM_RST: J3.4, U1.39
/V_SIM: J3.3, U1.38
GND: C1.2, C2.2, C3.2, J1.GND1, J1.GND2, J1.GND3, J1.GND4, J3.19, J3.20, J3.21, J3.22, SW1.1, U1.2, U1.43, U1.47, U1.48, U1.51, U1.52, U1.54, U1.59, U1.60, U1.61, U1.62, U1.63, U1.64, U1.65, U1.66, U1.71, U1.72, U1.73, U1.74, U1.81, U1.82, U1.83, U1.92, U1.93, U1.94
unnamed: C2.1, R1.2, U1.53
unnamed: C3.1, J1.P, R1.1

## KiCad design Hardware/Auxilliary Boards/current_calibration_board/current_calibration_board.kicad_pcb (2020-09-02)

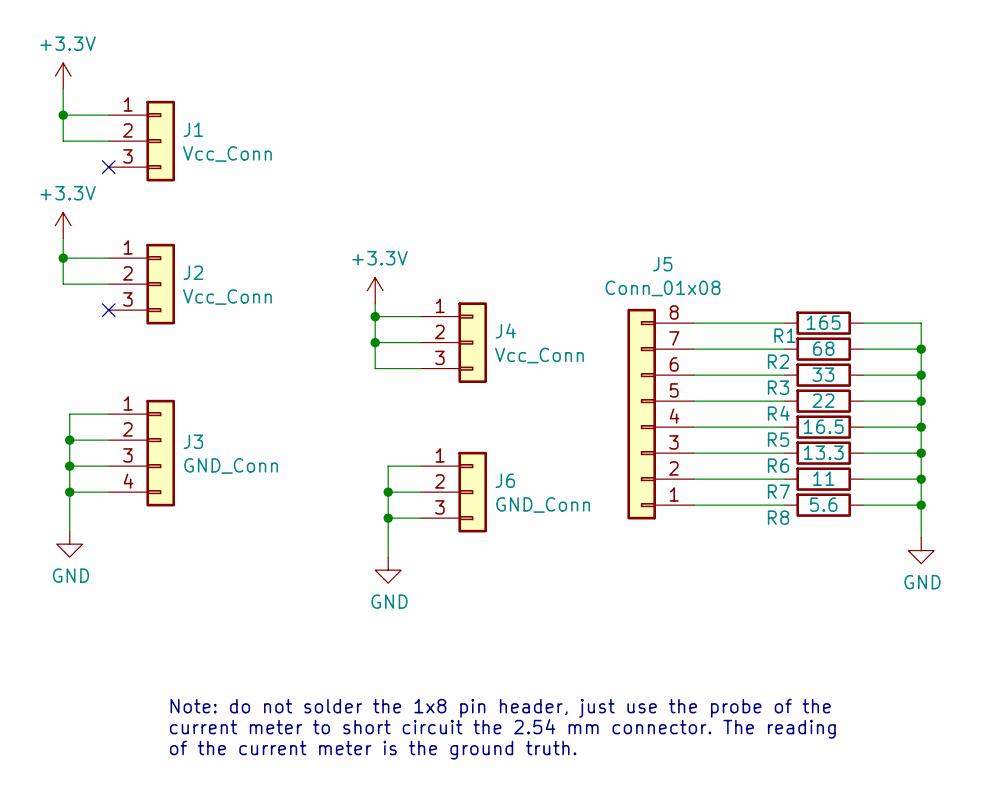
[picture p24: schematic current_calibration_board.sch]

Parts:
J1, J2: Vcc_Conn; PinHeader_1x03_P1.27mm_Vertical
J3: GND_Conn; PinHeader_1x04_P1.27mm_Vertical
J4: Vcc_Conn; PinHeader_1x03_P2.54mm_Vertical
J5: Conn_01x08; PinHeader_1x08_P2.54mm_Vertical
J6: GND_Conn; PinHeader_1x03_P2.54mm_Vertical
R1: 165; R_0805_2012Metric_Pad1.15x1.40mm_HandSolder
R2: 68; R_1206_3216Metric_Pad1.42x1.75mm_HandSolder
R3: 33; R_1210_3225Metric_Pad1.42x2.65mm_HandSolder
R4: 22; R_1210_3225Metric_Pad1.42x2.65mm_HandSolder
R5: 16.5; R_2512_6332Metric_Pad1.52x3.35mm_HandSolder
R6: 13.3; R_2512_6332Metric_Pad1.52x3.35mm_HandSolder
R7: 11; R_2512_6332Metric_Pad1.52x3.35mm_HandSolder
R8: 5.6; Resistor_SMD_1225_2W

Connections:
+3V3: J1.1, J1.2, J2.1, J2.2, J4.1, J4.2, J4.3
GND: J3.1, J3.2, J3.3, J3.4, J6.1, J6.2, J6.3, R1.1, R2.1, R3.1, R4.1, R5.1, R6.1, R7.1, R8.1
unnamed: J5.1, R8.2
unnamed: J5.2, R7.2
unnamed: J5.3, R6.2
unnamed: J5.4, R5.2
unnamed: J5.5, R4.2
unnamed: J5.6, R3.2
unnamed: J5.7, R2.2
unnamed: J5.8, R1.2

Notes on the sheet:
Note: do not solder the 1x8 pin header, just use the probe of the current meter to short circuit the 2.54 mm connector. The reading of the current meter is the ground truth.

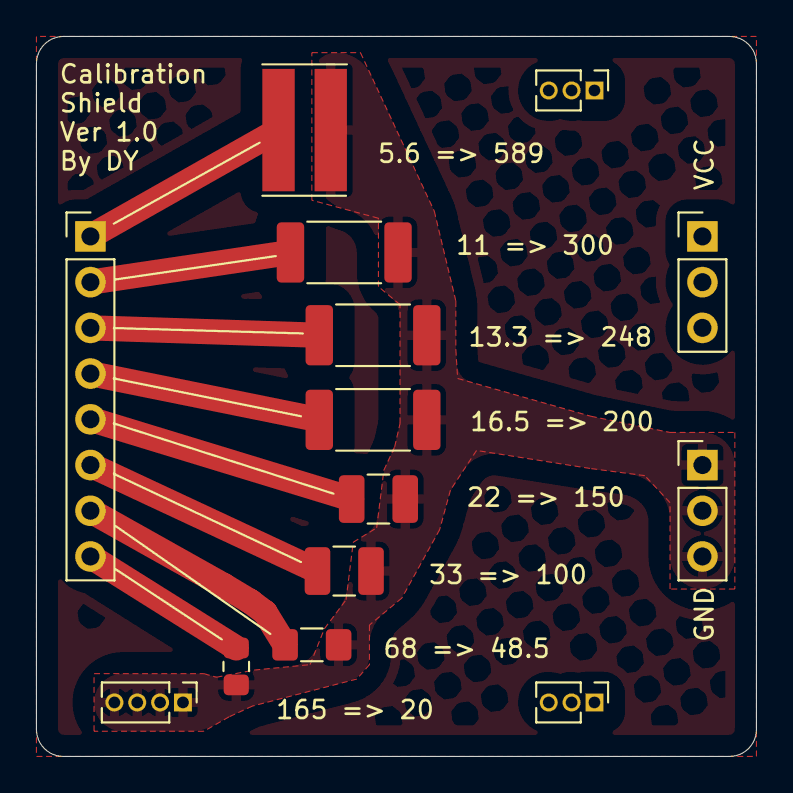
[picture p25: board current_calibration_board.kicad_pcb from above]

Board: 2 copper layers, 40.0 x 40.0 mm, 14 parts (0 on the bottom side), 10 nets.

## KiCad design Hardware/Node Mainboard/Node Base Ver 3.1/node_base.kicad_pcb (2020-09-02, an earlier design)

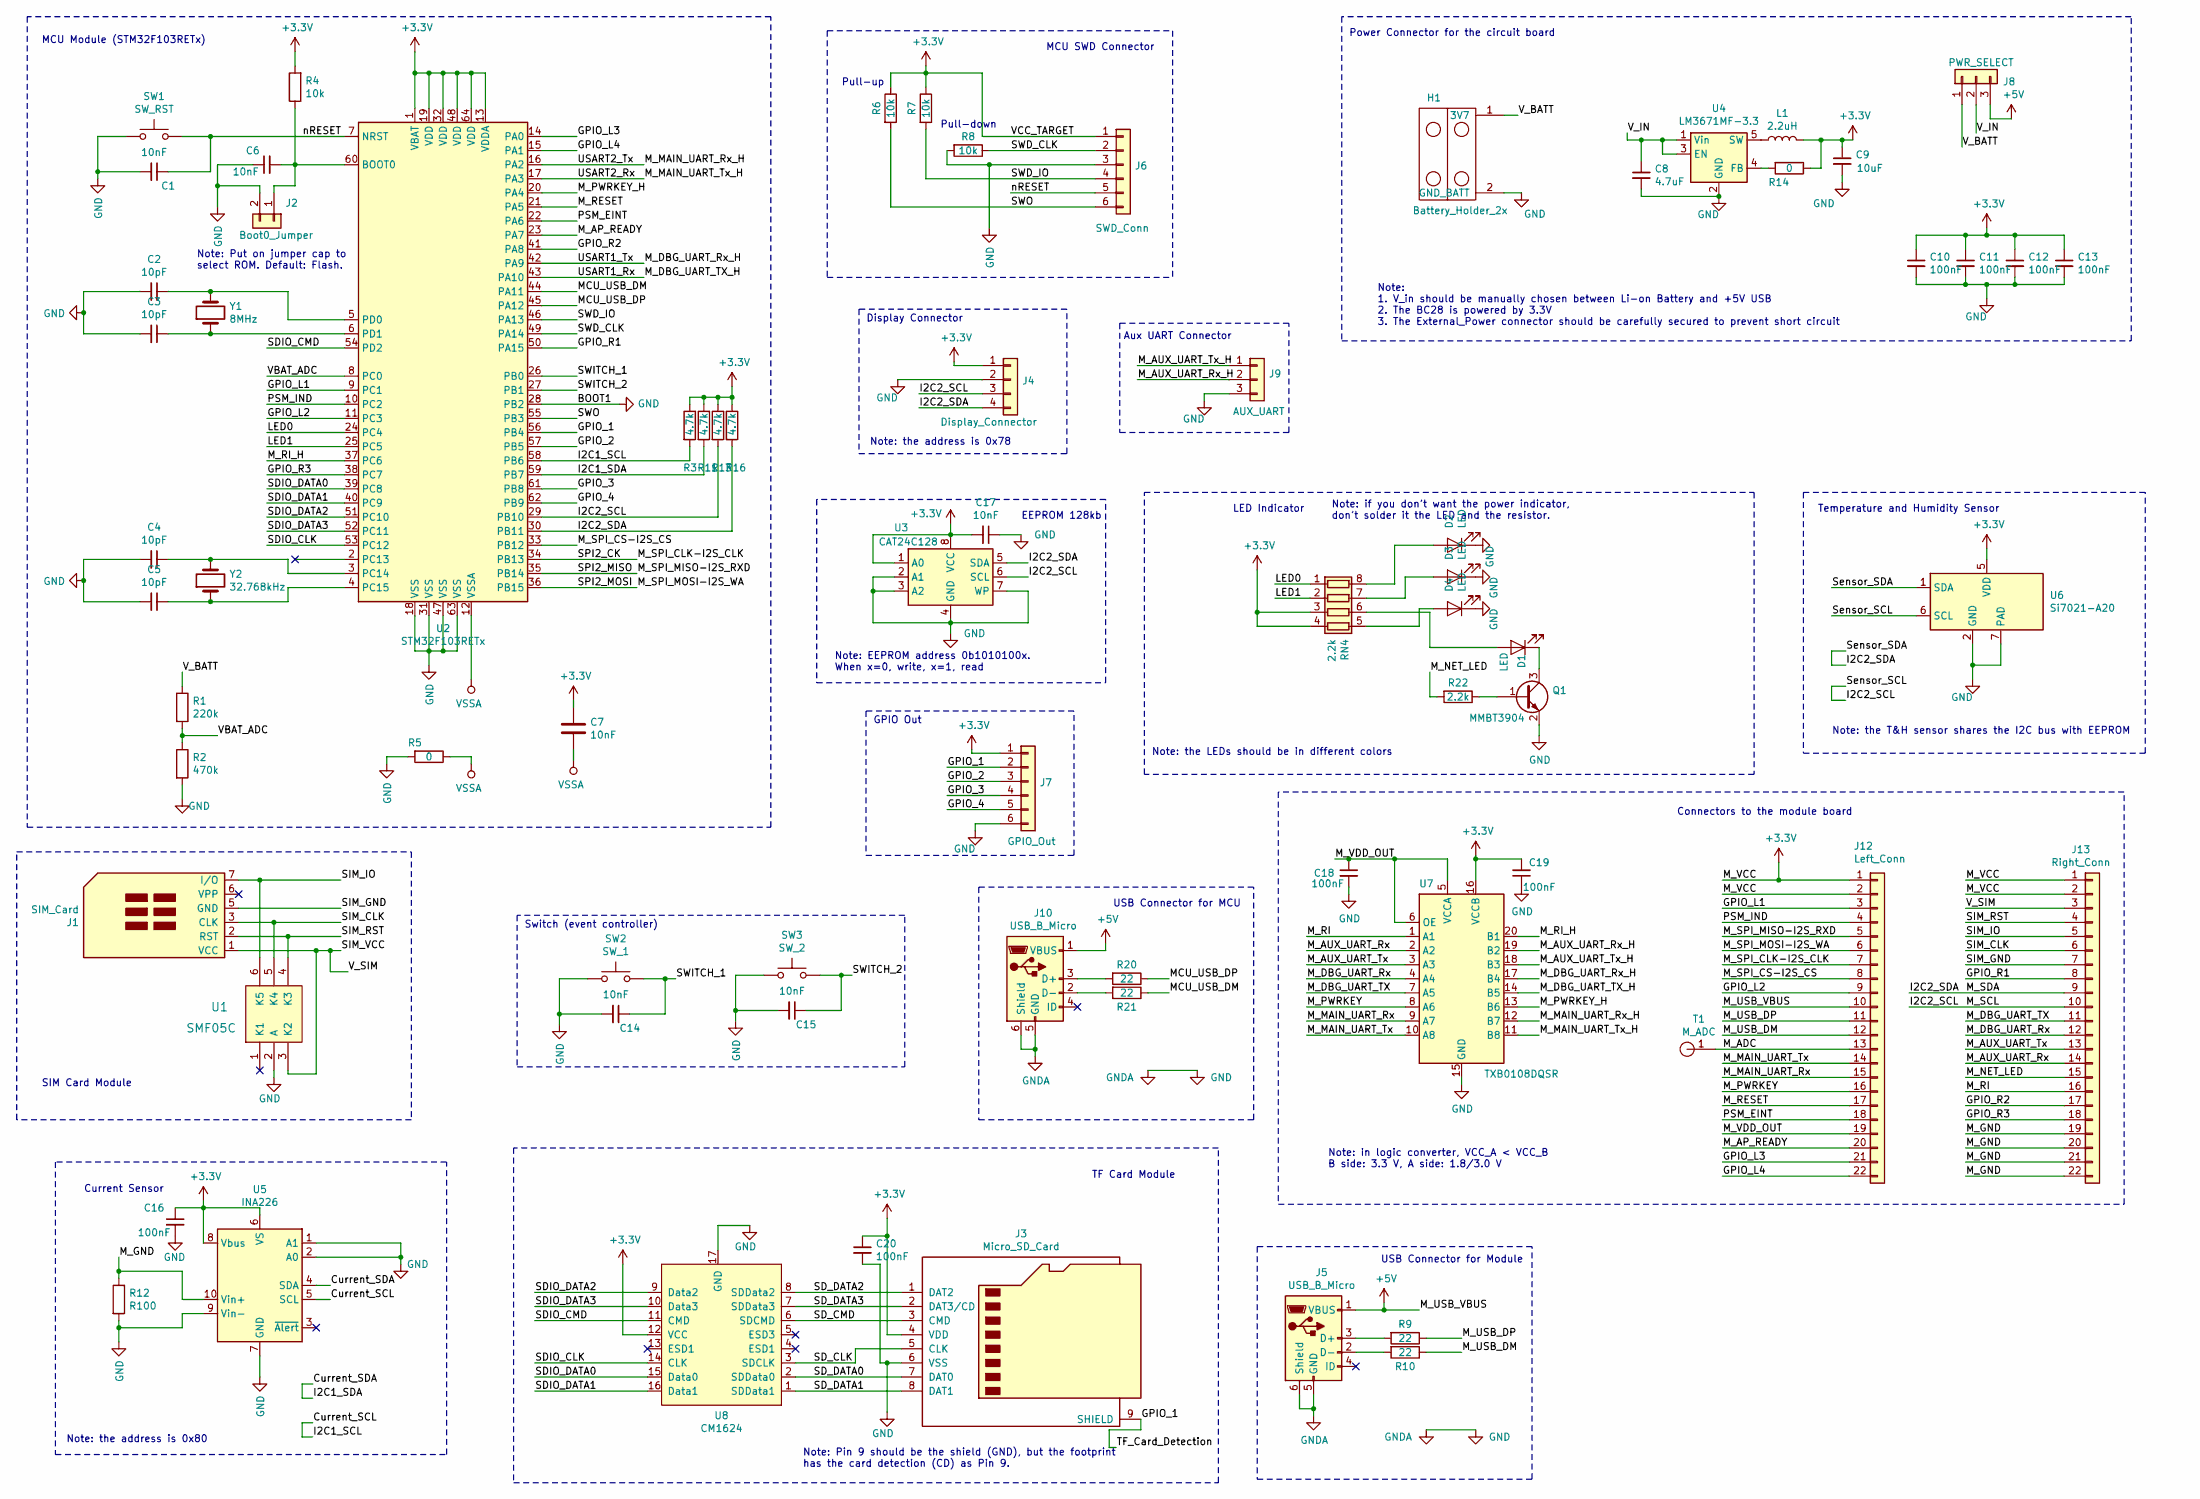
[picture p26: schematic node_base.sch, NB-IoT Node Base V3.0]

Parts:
C1, C6, C7, C14, C15, C17: 10nF; C_0603_1608Metric
C2, C3, C4, C5: 10pF; C_0603_1608Metric
C8: 4.7uF; C_0805_2012Metric
C9: 10uF; C_0805_2012Metric
C10, C11, C12, C13, C16, C18, C19, C20: 100nF; C_0603_1608Metric
D1, D2, D3, D4: LED; LED_0805_2012Metric
H1: Battery_Holder_2x; 18650_Battery_Holder_2x
J1: SIM_Card; Nano Sim Socket 1.1H, 6P
J2: Boot0_Jumper; PinHeader_1x02_P1.27mm_Vertical
J3: Micro_SD_Card; TF_Card_Socket
J4: Display_Connector; PinSocket_1x04_P1.27mm_Vertical
J5, J10: USB_B_Micro; USB_Micro-B_Molex-105017-0001
J6: SWD_Conn; PinSocket_1x06_P1.27mm_Vertical
J7: GPIO_Out; PinSocket_1x06_P1.27mm_Vertical
J8: PWR_SELECT; PinHeader_1x03_P2.54mm_Vertical
J9: AUX_UART; PinSocket_1x03_P1.27mm_Vertical
J12: Left_Conn; PinHeader_1x22_P1.27mm_Vertical
J13: Right_Conn; PinHeader_1x22_P1.27mm_Vertical
L1: 2.2uH; L_Sumida_CDRH2D14_3.2x3.2x1.55mm
Q1: MMBT3904; SOT-23
R1: 220k; R_0603_1608Metric
R2: 470k; R_0603_1608Metric
R3, R11, R13, R16: 4.7k; R_0603_1608Metric
R4, R6, R7, R8: 10k; R_0603_1608Metric
R5, R14: 0; R_0603_1608Metric
R9, R10, R20, R21: 22; R_0603_1608Metric
R12: R100; R_1206_3216Metric
R22: 2.2k; R_0603_1608Metric_Pad1.05x0.95mm_HandSolder
RN4: 2.2k; R_Array_Convex_4x0603
SW1: SW_RST; SW_SPST_FSMSM
SW2: SW_1; SW_SPST_FSMSM
SW3: SW_2; SW_SPST_FSMSM
T1: M_ADC; test_pad
U1: SMF05C
U2: STM32F103RETx; LQFP-64_10x10mm_P0.5mm
U3: CAT24C128; SOIC-8_3.9x4.9mm_P1.27mm
U4: LM3671MF-3.3; TSOT-23-5
U5: INA226; VSSOP-10_3x3mm_P0.5mm
U6: Si7021-A20; DFN-6-1EP_3x3mm_P1mm_EP1.5x2.4mm
U7: TXB0108DQSR; USON-20_2x4mm_P0.4mm
U8: CM1624; UDFN-16_3.3x1.35mm_0.4Pitch
Y1: 8MHz; Crystal_SMD_5032-2Pin_5.0x3.2mm
Y2: 32.768kHz; Crystal_SMD_3215-2Pin_3.2x1.5mm

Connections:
+3V3: C7.1, C9.1, C10.1, C11.1, C12.1, C13.1, C16.1, C17.2, C19.2, C20.1, J3.4 (VDD), J4.1, J6.1, J7.1, J12.1, J12.2, J13.1, J13.2, L1.2, R3.1, R4.2, R6.1, R7.1, R11.1, R13.1, R14.1, R16.1, RN4.3 (R3.1), RN4.4 (R4.1), U2.1 (VBAT), U2.13 (VDDA), U2.19 (VDD), U2.32 (VDD), U2.48 (VDD), U2.64 (VDD), U3.1 (A0), U3.8 (VCC), U5.6 (VS), U5.8 (Vbus), U6.5 (VDD), U7.16 (VCCB), U8.12 (VCC)
+5V: J5.1 (VBUS), J8.3, J10.1 (VBUS), J12.10
/Current_SCL: R3.2, U2.58 (PB6), U5.5 (SCL)
/Current_SDA: R11.2, U2.59 (PB7), U5.4 (SDA)
/GPIO_1: J3.9 (SHIELD), J7.2, U2.56 (PB4)
/GPIO_2: J7.3, U2.57 (PB5)
/GPIO_3: J7.4, U2.61 (PB8)
/GPIO_4: J7.5, U2.62 (PB9)
/GPIO_L1: J12.3, U2.9 (PC1)
/GPIO_L2: J12.9, U2.11 (PC3)
/GPIO_L3: J12.21, U2.14 (PA0)
/GPIO_L4: J12.22, U2.15 (PA1)
/GPIO_R1: J13.8, U2.50 (PA15)
/GPIO_R2: J13.17, U2.41 (PA8)
/GPIO_R3: J13.18, U2.38 (PC7)
/I2C2_SCL: J4.3, J13.10, R13.2, U2.29 (PB10), U3.6 (SCL), U6.6 (SCL)
/I2C2_SDA: J4.4, J13.9, R16.2, U2.30 (PB11), U3.5 (SDA), U6.1 (SDA)
/LED0: RN4.1 (R1.1), U2.24 (PC4)
/LED1: RN4.2 (R2.1), U2.25 (PC5)
/MCU_USB_DM: R21.1, U2.44 (PA11)
/MCU_USB_DP: R20.1, U2.45 (PA12)
/M_ADC: J12.13, T1.1
/M_AP_READY: J12.20, U2.23 (PA7)
/M_AUX_UART_Rx: J13.14, U7.2 (A2)
/M_AUX_UART_Rx_H: J9.2, U7.19 (B2)
/M_AUX_UART_Tx: J13.13, U7.3 (A3)
/M_AUX_UART_Tx_H: J9.1, U7.18 (B3)
/M_DBG_UART_Rx: J13.12, U7.4 (A4)
/M_DBG_UART_Rx_H: U2.42 (PA9), U7.17 (B4)
/M_DBG_UART_TX: J13.11, U7.7 (A5)
/M_DBG_UART_TX_H: U2.43 (PA10), U7.14 (B5)
/M_GND: J13.19, J13.20, J13.21, J13.22, R12.1, U5.10 (Vin+)
/M_MAIN_UART_Rx: J12.15, U7.9 (A7)
/M_MAIN_UART_Rx_H: U2.16 (PA2), U7.12 (B7)
/M_MAIN_UART_Tx: J12.14, U7.10 (A8)
/M_MAIN_UART_Tx_H: U2.17 (PA3), U7.11 (B8)
/M_NET_LED: J13.15, R22.2
/M_PWRKEY: J12.16, U7.8 (A6)
/M_PWRKEY_H: U2.20 (PA4), U7.13 (B6)
/M_RESET: J12.17, U2.21 (PA5)
/M_RI: J13.16, U7.1 (A1)
/M_RI_H: U2.37 (PC6), U7.20 (B1)
/M_SPI_CLK-I2S_CLK: J12.7, U2.34 (PB13)
/M_SPI_CS-I2S_CS: J12.8, U2.33 (PB12)
/M_SPI_MISO-I2S_RXD: J12.5, U2.35 (PB14)
/M_SPI_MOSI-I2S_WA: J12.6, U2.36 (PB15)
/M_USB_DM: J12.12, R10.1
/M_USB_DP: J12.11, R9.1
/M_VDD_OUT: C18.1, J12.19, U7.5 (VCCA), U7.6 (OE)
/PSM_EINT: J12.18, U2.22 (PA6)
/PSM_IND: J12.4, U2.10 (PC2)
/SDIO_CLK: U2.53 (PC12), U8.14 (CLK)
/SDIO_CMD: U2.54 (PD2), U8.11 (CMD)
/SDIO_DATA0: U2.39 (PC8), U8.15 (Data0)
/SDIO_DATA1: U2.40 (PC9), U8.16 (Data1)
/SDIO_DATA2: U2.51 (PC10), U8.9 (Data2)
/SDIO_DATA3: U2.52 (PC11), U8.10 (Data3)
/SD_CLK: J3.5 (CLK), U8.3 (SDCLK)
/SD_CMD: J3.3 (CMD), U8.6 (SDCMD)
/SD_DATA0: J3.7 (DAT0), U8.2 (SDData0)
/SD_DATA1: J3.8 (DAT1), U8.1 (SDData1)
/SD_DATA2: J3.1 (DAT2), U8.8 (SDData2)
/SD_DATA3: J3.2 (DAT3/CD), U8.7 (SDData3)
/SIM_CLK: J1.3 (CLK), J13.6, U1.5 (K4)
/SIM_GND: J1.5 (GND), J13.7
/SIM_IO: J1.7 (I/O), J13.5, U1.6 (K5)
/SIM_RST: J1.2 (RST), J13.4, U1.4 (K3)
/SIM_VCC: J1.1 (VCC), J13.3, U1.3 (K2)
/SWD_CLK: J6.2, R8.1, U2.49 (PA14)
/SWD_IO: J6.4, R7.2, U2.46 (PA13)
/SWITCH_1: C14.1, SW2.2, U2.26 (PB0)
/SWITCH_2: C15.1, SW3.2, U2.27 (PB1)
/SWO: J6.6, R6.2, U2.55 (PB3)
/VBAT_ADC: R1.2, R2.1, U2.8 (PC0)
/V_BATT: H1.1 (3V7), J8.1, R1.1
/V_IN: C8.1, J8.2, U4.1 (Vin), U4.3 (EN)
/nRESET: C1.1, J6.5, SW1.2, U2.7 (NRST)
GND: C1.2, C2.2, C3.2, C4.2, C5.2, C6.1, C8.2, C9.2, C10.2, C11.2, C12.2, C13.2, C14.2, C15.2, C16.2, C17.1, C18.2, C19.1, C20.2, D2.1 (K), D3.1 (K), D4.1 (K), H1.2 (GND_BATT), J2.2, J3.6 (VSS), J4.2, J5.5 (GND), J5.6 (Shield), J6.3, J7.6, J9.3, J10.5 (GND), J10.6 (Shield), Q1.2 (E), R2.2, R5.2, R8.2, R12.2, SW1.1, SW2.1, SW3.1, U1.2 (A), U2.18 (VSS), U2.28 (PB2), U2.31 (VSS), U2.47 (VSS), U2.63 (VSS), U3.2 (A1), U3.3 (A2), U3.4 (GND), U3.7 (WP), U4.2 (GND), U5.1 (A1), U5.2 (A0), U5.7 (GND), U5.9 (Vin-), U6.2 (GND), U6.7 (PAD), U7.15 (GND), U8.17 (GND)
unnamed: C2.1, U2.5 (PD0), Y1.2
unnamed: C3.1, U2.6 (PD1), Y1.1
unnamed: C4.1, U2.3 (PC14), Y2.2
unnamed: C5.1, U2.4 (PC15), Y2.1
unnamed: C6.2, J2.1, R4.1, U2.60 (BOOT0)
unnamed: D1.1 (K), Q1.3 (C)
unnamed: D1.2 (A), RN4.6 (R3.2)
unnamed: D2.2 (A), RN4.8 (R1.2)
unnamed: D3.2 (A), RN4.7 (R2.2)
unnamed: D4.2 (A), RN4.5 (R4.2)
unnamed: J5.2 (D-), R10.2
unnamed: J5.3 (D+), R9.2
unnamed: J10.2 (D-), R21.2
unnamed: J10.3 (D+), R20.2
unnamed: L1.1, U4.5 (SW)
unnamed: Q1.1 (B), R22.1
unnamed: R14.2, U4.4 (FB)
VSSA: C7.2, R5.1, U2.12 (VSSA)

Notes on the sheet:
Note: Put on jumper cap to select ROM. Default: Flash.
MCU Module (STM32F103RETx)
Power Connector for the circuit board
Note: 1. V_in should be manually chosen between Li-on Battery and +5V USB 2. The BC28 is powered by 3.3V 3. The External_Power connector should be carefully secured to prevent short circuit
Pull-down
Pull-up
MCU SWD Connector
EEPROM 128kb
Note: the LEDs should be in different colors
LED Indicator
Note: if you don’t want the power indicator, don’t solder it the LED and the resistor.
Note: the T&H sensor shares the I2C bus with EEPROM
Connectors to the module board
Current Sensor
SIM Card Module
Temperature and Humidity Sensor
Switch (event controller)
Note: Pin 9 should be the shield (GND), but the footprint has the card detection (CD) as Pin 9.
TF Card Module
Note: EEPROM address 0b1010100x. When x=0, write, x=1, read
Display Connector
Note: the address is 0x78
Note: the address is 0x80
Aux UART Connector
USB Connector for MCU
USB Connector for Module
GPIO Out
Note: in logic converter, VCC_A < VCC_B B side: 3.3 V, A side: 1.8/3.0 V

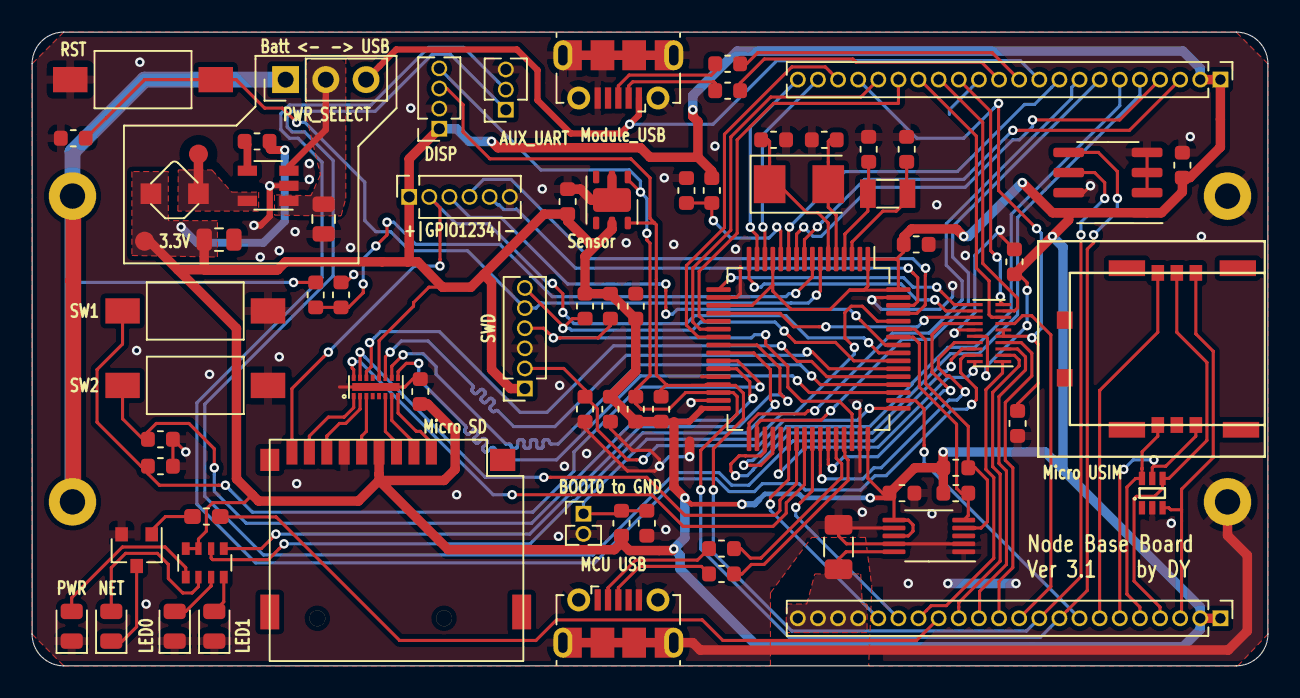
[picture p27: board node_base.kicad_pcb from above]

Board: 2 copper layers, 78.0 x 40.0 mm, 72 parts (1 on the bottom side), 96 nets.

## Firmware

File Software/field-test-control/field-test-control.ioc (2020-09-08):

#MicroXplorer Configuration settings - do not modify
ADC1.Channel-0\#ChannelRegularConversion=ADC_CHANNEL_10
ADC1.Channel-1\#ChannelRegularConversion=ADC_CHANNEL_10
ADC1.Channel-4\#ChannelRegularConversion=ADC_CHANNEL_10
ADC1.Channel-5\#ChannelRegularConversion=ADC_CHANNEL_10
ADC1.EnableAnalogWatchDog=false
ADC1.IPParameters=Rank-0\#ChannelRegularConversion,Channel-0\#ChannelRegularConversion,SamplingTime-0\#ChannelRegularConversion,NbrOfConversionFlag,master,EnableAnalogWatchDog,NbrOfConversion,Rank-1\#ChannelRegularConversion,Channel-1\#ChannelRegularConversion,SamplingTime-1\#ChannelRegularConversion,Rank-4\#ChannelRegularConversion,Channel-4\#ChannelRegularConversion,SamplingTime-4\#ChannelRegularConversion,Rank-5\#ChannelRegularConversion,Channel-5\#ChannelRegularConversion,SamplingTime-5\#ChannelRegularConversion
ADC1.NbrOfConversion=4
ADC1.NbrOfConversionFlag=1
ADC1.Rank-0\#ChannelRegularConversion=1
ADC1.Rank-1\#ChannelRegularConversion=2
ADC1.Rank-4\#ChannelRegularConversion=3
ADC1.Rank-5\#ChannelRegularConversion=4
ADC1.SamplingTime-0\#ChannelRegularConversion=ADC_SAMPLETIME_55CYCLES_5
ADC1.SamplingTime-1\#ChannelRegularConversion=ADC_SAMPLETIME_1CYCLE_5
ADC1.SamplingTime-4\#ChannelRegularConversion=ADC_SAMPLETIME_1CYCLE_5
ADC1.SamplingTime-5\#ChannelRegularConversion=ADC_SAMPLETIME_1CYCLE_5
ADC1.master=1
Dma.MEMTOMEM.4.Direction=DMA_MEMORY_TO_MEMORY
Dma.MEMTOMEM.4.Instance=DMA1_Channel1
Dma.MEMTOMEM.4.MemDataAlignment=DMA_MDATAALIGN_BYTE
Dma.MEMTOMEM.4.MemInc=DMA_MINC_ENABLE
Dma.MEMTOMEM.4.Mode=DMA_NORMAL
Dma.MEMTOMEM.4.PeriphDataAlignment=DMA_PDATAALIGN_BYTE
Dma.MEMTOMEM.4.PeriphInc=DMA_PINC_ENABLE
Dma.MEMTOMEM.4.Priority=DMA_PRIORITY_LOW
Dma.MEMTOMEM.4.RequestParameters=Instance,Direction,PeriphInc,MemInc,PeriphDataAlignment,MemDataAlignment,Mode,Priority
Dma.Request0=SDIO
Dma.Request1=USART2_RX
Dma.Request2=USART2_TX
Dma.Request3=USART1_RX
Dma.Request4=MEMTOMEM
Dma.RequestsNb=5
Dma.SDIO.0.Direction=DMA_MEMORY_TO_PERIPH
Dma.SDIO.0.Instance=DMA2_Channel4
Dma.SDIO.0.MemDataAlignment=DMA_MDATAALIGN_WORD
Dma.SDIO.0.MemInc=DMA_MINC_ENABLE
Dma.SDIO.0.Mode=DMA_CIRCULAR
Dma.SDIO.0.PeriphDataAlignment=DMA_PDATAALIGN_WORD
Dma.SDIO.0.PeriphInc=DMA_PINC_DISABLE
Dma.SDIO.0.Priority=DMA_PRIORITY_LOW
Dma.SDIO.0.RequestParameters=Instance,Direction,PeriphInc,MemInc,PeriphDataAlignment,MemDataAlignment,Mode,Priority
Dma.USART1_RX.3.Direction=DMA_PERIPH_TO_MEMORY
Dma.USART1_RX.3.Instance=DMA1_Channel5
Dma.USART1_RX.3.MemDataAlignment=DMA_MDATAALIGN_BYTE
Dma.USART1_RX.3.MemInc=DMA_MINC_ENABLE
Dma.USART1_RX.3.Mode=DMA_NORMAL
Dma.USART1_RX.3.PeriphDataAlignment=DMA_PDATAALIGN_BYTE
Dma.USART1_RX.3.PeriphInc=DMA_PINC_DISABLE
Dma.USART1_RX.3.Priority=DMA_PRIORITY_MEDIUM
Dma.USART1_RX.3.RequestParameters=Instance,Direction,PeriphInc,MemInc,PeriphDataAlignment,MemDataAlignment,Mode,Priority
Dma.USART2_RX.1.Direction=DMA_PERIPH_TO_MEMORY
Dma.USART2_RX.1.Instance=DMA1_Channel6
Dma.USART2_RX.1.MemDataAlignment=DMA_MDATAALIGN_BYTE
Dma.USART2_RX.1.MemInc=DMA_MINC_ENABLE
Dma.USART2_RX.1.Mode=DMA_NORMAL
Dma.USART2_RX.1.PeriphDataAlignment=DMA_PDATAALIGN_BYTE
Dma.USART2_RX.1.PeriphInc=DMA_PINC_DISABLE
Dma.USART2_RX.1.Priority=DMA_PRIORITY_LOW
Dma.USART2_RX.1.RequestParameters=Instance,Direction,PeriphInc,MemInc,PeriphDataAlignment,MemDataAlignment,Mode,Priority
Dma.USART2_TX.2.Direction=DMA_MEMORY_TO_PERIPH
Dma.USART2_TX.2.Instance=DMA1_Channel7
Dma.USART2_TX.2.MemDataAlignment=DMA_MDATAALIGN_BYTE
Dma.USART2_TX.2.MemInc=DMA_MINC_ENABLE
Dma.USART2_TX.2.Mode=DMA_NORMAL
Dma.USART2_TX.2.PeriphDataAlignment=DMA_PDATAALIGN_BYTE
Dma.USART2_TX.2.PeriphInc=DMA_PINC_DISABLE
Dma.USART2_TX.2.Priority=DMA_PRIORITY_LOW
Dma.USART2_TX.2.RequestParameters=Instance,Direction,PeriphInc,MemInc,PeriphDataAlignment,MemDataAlignment,Mode,Priority
FATFS.BSP.number=1
FATFS.IPParameters=_CODE_PAGE,_USE_LFN
FATFS._CODE_PAGE=936
FATFS._USE_LFN=2
FATFS0.BSP.STBoard=false
FATFS0.BSP.api=Unknown
FATFS0.BSP.component=
FATFS0.BSP.condition=
FATFS0.BSP.i2caddr=0
FATFS0.BSP.i2creg=
FATFS0.BSP.instance=PB4
FATFS0.BSP.ip=GPIO
FATFS0.BSP.mode=Input
FATFS0.BSP.name=Detect_SDIO
FATFS0.BSP.semaphore=
FATFS0.BSP.solution=PB4
File.Version=6
I2C1.I2C_Mode=I2C_Fast
I2C1.IPParameters=I2C_Mode
I2C2.I2C_Mode=I2C_Fast
I2C2.IPParameters=I2C_Mode
KeepUserPlacement=false
Mcu.Family=STM32F1
Mcu.IP0=ADC1
Mcu.IP1=DMA
Mcu.IP10=SYS
Mcu.IP11=USART1
Mcu.IP12=USART2
Mcu.IP13=USB
Mcu.IP14=USB_DEVICE
Mcu.IP2=FATFS
Mcu.IP3=I2C1
Mcu.IP4=I2C2
Mcu.IP5=NVIC
Mcu.IP6=RCC
Mcu.IP7=RTC
Mcu.IP8=SDIO
Mcu.IP9=SPI2
Mcu.IPNb=15
Mcu.Name=STM32F103R(C-D-E)Tx
Mcu.Package=LQFP64
Mcu.Pin0=PC14-OSC32_IN
Mcu.Pin1=PC15-OSC32_OUT
Mcu.Pin10=PA2
Mcu.Pin11=PA3
Mcu.Pin12=PA4
Mcu.Pin13=PA5
Mcu.Pin14=PA6
Mcu.Pin15=PA7
Mcu.Pin16=PC4
Mcu.Pin17=PC5
Mcu.Pin18=PB0
Mcu.Pin19=PB1
Mcu.Pin2=PD0-OSC_IN
Mcu.Pin20=PB10
Mcu.Pin21=PB11
Mcu.Pin22=PB12
Mcu.Pin23=PB13
Mcu.Pin24=PB14
Mcu.Pin25=PB15
Mcu.Pin26=PC6
Mcu.Pin27=PC7
Mcu.Pin28=PC8
Mcu.Pin29=PC9
Mcu.Pin3=PD1-OSC_OUT
Mcu.Pin30=PA8
Mcu.Pin31=PA9
Mcu.Pin32=PA10
Mcu.Pin33=PA11
Mcu.Pin34=PA12
Mcu.Pin35=PA13
Mcu.Pin36=PA14
Mcu.Pin37=PA15
Mcu.Pin38=PC10
Mcu.Pin39=PC11
Mcu.Pin4=PC0
Mcu.Pin40=PC12
Mcu.Pin41=PD2
Mcu.Pin42=PB3
Mcu.Pin43=PB4
Mcu.Pin44=PB5
Mcu.Pin45=PB6
Mcu.Pin46=PB7
Mcu.Pin47=PB8
Mcu.Pin48=PB9
Mcu.Pin49=VP_FATFS_VS_SDIO
Mcu.Pin5=PC1
Mcu.Pin50=VP_RTC_VS_RTC_Activate
Mcu.Pin51=VP_SYS_VS_Systick
Mcu.Pin52=VP_USB_DEVICE_VS_USB_DEVICE_CDC_FS
Mcu.Pin6=PC2
Mcu.Pin7=PC3
Mcu.Pin8=PA0-WKUP
Mcu.Pin9=PA1
Mcu.PinsNb=53
Mcu.ThirdPartyNb=0
Mcu.UserConstants=
Mcu.UserName=STM32F103RETx
MxCube.Version=5.4.0
MxDb.Version=DB.5.0.40
NVIC.BusFault_IRQn=true\:0\:0\:false\:false\:true\:false\:false
NVIC.DMA1_Channel5_IRQn=true\:0\:0\:false\:false\:true\:false\:true
NVIC.DMA1_Channel6_IRQn=true\:0\:0\:false\:false\:true\:false\:true
NVIC.DMA1_Channel7_IRQn=true\:0\:0\:false\:false\:true\:false\:true
NVIC.DMA2_Channel4_5_IRQn=true\:2\:0\:true\:false\:true\:false\:true
NVIC.DebugMonitor_IRQn=true\:0\:0\:false\:false\:true\:false\:false
NVIC.EXTI0_IRQn=true\:3\:0\:true\:false\:true\:true\:true
NVIC.EXTI1_IRQn=true\:3\:0\:true\:false\:true\:true\:true
NVIC.ForceEnableDMAVector=true
NVIC.HardFault_IRQn=true\:0\:0\:false\:false\:true\:false\:false
NVIC.MemoryManagement_IRQn=true\:0\:0\:false\:false\:true\:false\:false
NVIC.NonMaskableInt_IRQn=true\:0\:0\:false\:false\:true\:false\:false
NVIC.PendSV_IRQn=true\:0\:0\:false\:false\:true\:false\:false
NVIC.PriorityGroup=NVIC_PRIORITYGROUP_4
NVIC.RTC_IRQn=true\:0\:0\:true\:false\:true\:true\:true
NVIC.SDIO_IRQn=true\:2\:0\:true\:false\:true\:true\:true
NVIC.SVCall_IRQn=true\:0\:0\:false\:false\:true\:false\:false
NVIC.SysTick_IRQn=true\:0\:0\:false\:false\:true\:false\:true
NVIC.USART2_IRQn=true\:1\:0\:true\:false\:true\:true\:true
NVIC.USB_LP_CAN1_RX0_IRQn=true\:0\:0\:false\:false\:true\:false\:true
NVIC.UsageFault_IRQn=true\:0\:0\:false\:false\:true\:false\:false
PA0-WKUP.GPIOParameters=GPIO_Label
PA0-WKUP.GPIO_Label=M_GPIO_L3
PA0-WKUP.Locked=true
PA0-WKUP.Signal=GPIO_Output
PA1.GPIOParameters=GPIO_PuPd,GPIO_Label
PA1.GPIO_Label=M_GPIO_L4
PA1.GPIO_PuPd=GPIO_NOPULL
PA1.Locked=true
PA1.Signal=GPIO_Output
PA10.Mode=Asynchronous
PA10.Signal=USART1_RX
PA11.Mode=Device
PA11.Signal=USB_DM
PA12.Mode=Device
PA12.Signal=USB_DP
PA13.Mode=Serial_Wire
PA13.Signal=SYS_JTMS-SWDIO
PA14.Mode=Serial_Wire
PA14.Signal=SYS_JTCK-SWCLK
PA15.GPIOParameters=GPIO_Label
PA15.GPIO_Label=M_GPIO_R1
PA15.Locked=true
PA15.Signal=GPIO_Output
PA2.Mode=Asynchronous
PA2.Signal=USART2_TX
PA3.Mode=Asynchronous
PA3.Signal=USART2_RX
PA4.GPIOParameters=PinState,GPIO_PuPd,GPIO_Label
PA4.GPIO_Label=M_PWRKEY
PA4.GPIO_PuPd=GPIO_PULLUP
PA4.Locked=true
PA4.PinState=GPIO_PIN_RESET
PA4.Signal=GPIO_Output
PA5.GPIOParameters=GPIO_PuPd,GPIO_Label
PA5.GPIO_Label=M_RESET
PA5.GPIO_PuPd=GPIO_PULLUP
PA5.Locked=true
PA5.Signal=GPIO_Output
PA6.GPIOParameters=GPIO_Label
PA6.GPIO_Label=M_WAKEUP_FROM_PSM
PA6.Locked=true
PA6.Signal=GPIO_Output
PA7.GPIOParameters=GPIO_Label
PA7.GPIO_Label=M_AP_READY
PA7.Locked=true
PA7.Signal=GPIO_Output
PA8.GPIOParameters=GPIO_Label
PA8.GPIO_Label=M_GPIO_R2
PA8.Locked=true
PA8.Signal=GPIO_Output
PA9.Mode=Asynchronous
PA9.Signal=USART1_TX
PB0.GPIOParameters=GPIO_PuPd,GPIO_Label,GPIO_ModeDefaultEXTI
PB0.GPIO_Label=BUTTON1
PB0.GPIO_ModeDefaultEXTI=GPIO_MODE_IT_FALLING
PB0.GPIO_PuPd=GPIO_PULLUP
PB0.Locked=true
PB0.Signal=GPXTI0
PB1.GPIOParameters=GPIO_PuPd,GPIO_Label,GPIO_ModeDefaultEXTI
PB1.GPIO_Label=BUTTON2
PB1.GPIO_ModeDefaultEXTI=GPIO_MODE_IT_FALLING
PB1.GPIO_PuPd=GPIO_PULLUP
PB1.Locked=true
PB1.Signal=GPXTI1
PB10.GPIOParameters=GPIO_Label
PB10.GPIO_Label=BUS_SCL
PB10.Mode=I2C
PB10.Signal=I2C2_SCL
PB11.GPIOParameters=GPIO_Label
PB11.GPIO_Label=BUS_SDA
PB11.Mode=I2C
PB11.Signal=I2C2_SDA
PB12.GPIOParameters=GPIO_Label
PB12.GPIO_Label=M_SPI_CS
PB12.Locked=true
PB12.Signal=GPIO_Output
PB13.Mode=Full_Duplex_Master
PB13.Signal=SPI2_SCK
PB14.Mode=Full_Duplex_Master
PB14.Signal=SPI2_MISO
PB15.Mode=Full_Duplex_Master
PB15.Signal=SPI2_MOSI
PB3.Locked=true
PB3.Signal=SYS_JTDO-TRACESWO
PB4.GPIOParameters=GPIO_Label
PB4.GPIO_Label=TF_DET
PB4.Locked=true
PB4.Signal=GPIO_Input
PB5.GPIOParameters=GPIO_Label
PB5.GPIO_Label=GPIO_2
PB5.Locked=true
PB5.Signal=GPIO_Output
PB6.GPIOParameters=GPIO_Label
PB6.GPIO_Label=INA226_SCL
PB6.Locked=true
PB6.Mode=I2C
PB6.Signal=I2C1_SCL
PB7.GPIOParameters=GPIO_Label
PB7.GPIO_Label=INA226_SDA
PB7.Locked=true
PB7.Mode=I2C
PB7.Signal=I2C1_SDA
PB8.GPIOParameters=GPIO_Label
PB8.GPIO_Label=GPIO_3
PB8.Locked=true
PB8.Signal=GPIO_Output
PB9.GPIOParameters=GPIO_Label
PB9.GPIO_Label=GPIO_4
PB9.Locked=true
PB9.Signal=GPIO_Output
PC0.GPIOParameters=GPIO_Label
PC0.GPIO_Label=V_BATT_ADC
PC0.Signal=ADCx_IN10
PC1.GPIOParameters=GPIO_Label
PC1.GPIO_Label=M_GPIO_L1
PC1.Locked=true
PC1.Signal=GPIO_Output
PC10.Mode=SD_4_bits_Wide_bus
PC10.Signal=SDIO_D2
PC11.Mode=SD_4_bits_Wide_bus
PC11.Signal=SDIO_D3
PC12.Mode=SD_4_bits_Wide_bus
PC12.Signal=SDIO_CK
PC14-OSC32_IN.Mode=LSE-External-Oscillator
PC14-OSC32_IN.Signal=RCC_OSC32_IN
PC15-OSC32_OUT.Mode=LSE-External-Oscillator
PC15-OSC32_OUT.Signal=RCC_OSC32_OUT
PC2.GPIOParameters=GPIO_Label
PC2.GPIO_Label=M_PSM_IND
PC2.Locked=true
PC2.Signal=GPIO_Input
PC3.GPIOParameters=GPIO_Label
PC3.GPIO_Label=M_GPIO_L2
PC3.Locked=true
PC3.Signal=GPIO_Output
PC4.GPIOParameters=GPIO_Label
PC4.GPIO_Label=LED0
PC4.Locked=true
PC4.Signal=GPIO_Output
PC5.GPIOParameters=GPIO_Label
PC5.GPIO_Label=LED1
PC5.Locked=true
PC5.Signal=GPIO_Output
PC6.GPIOParameters=GPIO_Label
PC6.GPIO_Label=M_RI
PC6.Locked=true
PC6.Signal=GPIO_Input
PC7.GPIOParameters=GPIO_Label
PC7.GPIO_Label=M_GPIO_R3
PC7.Locked=true
PC7.Signal=GPIO_Output
PC8.Mode=SD_4_bits_Wide_bus
PC8.Signal=SDIO_D0
PC9.Mode=SD_4_bits_Wide_bus
PC9.Signal=SDIO_D1
PCC.Checker=false
PCC.Line=STM32F103
PCC.MCU=STM32F103R(C-D-E)Tx
PCC.PartNumber=STM32F103RETx
PCC.Seq0=0
PCC.Series=STM32F1
PCC.Temperature=25
PCC.Vdd=3.3
PD0-OSC_IN.Mode=HSE-External-Oscillator
PD0-OSC_IN.Signal=RCC_OSC_IN
PD1-OSC_OUT.Mode=HSE-External-Oscillator
PD1-OSC_OUT.Signal=RCC_OSC_OUT
PD2.Mode=SD_4_bits_Wide_bus
PD2.Signal=SDIO_CMD
PinOutPanel.RotationAngle=0
ProjectManager.AskForMigrate=true
ProjectManager.BackupPrevious=false
ProjectManager.CompilerOptimize=6
ProjectManager.ComputerToolchain=false
ProjectManager.CoupleFile=false
ProjectManager.CustomerFirmwarePackage=
ProjectManager.DefaultFWLocation=true
ProjectManager.DeletePrevious=true
ProjectManager.DeviceId=STM32F103RETx
ProjectManager.FirmwarePackage=STM32Cube FW_F1 V1.8.0
ProjectManager.FreePins=false
ProjectManager.HalAssertFull=false
ProjectManager.HeapSize=0x400
ProjectManager.KeepUserCode=true
ProjectManager.LastFirmware=true
ProjectManager.LibraryCopy=1
ProjectManager.MainLocation=Core/Src
ProjectManager.NoMain=false
ProjectManager.PreviousToolchain=SW4STM32
ProjectManager.ProjectBuild=false
ProjectManager.ProjectFileName=field-test-control.ioc
ProjectManager.ProjectName=field-test-control
ProjectManager.StackSize=0x1000
ProjectManager.TargetToolchain=SW4STM32
ProjectManager.ToolChainLocation=
ProjectManager.UnderRoot=true
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

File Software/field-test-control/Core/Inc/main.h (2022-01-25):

/* USER CODE BEGIN Header */
/**
 ******************************************************************************
 * @file           : main.h
 * @brief          : Header for main.c file.
 *                   This file contains the common defines of the application.
 ******************************************************************************
 * @attention Include this file whenever you need the macros here.
 *
 * <h2><center>&copy; Copyright (c) 2019 STMicroelectronics.
 * All rights reserved.</center></h2>
 *
 * This software component is licensed by ST under Ultimate Liberty license
 * SLA0044, the "License"; You may not use this file except in compliance with
 * the License. You may obtain a copy of the License at:
 *                             www.st.com/SLA0044
 *
 ******************************************************************************
 */
/* USER CODE END Header */

/* Define to prevent recursive inclusion -------------------------------------*/
#ifndef __MAIN_H
#define __MAIN_H

#ifdef __cplusplus
extern "C" {
#endif

/* Includes ------------------------------------------------------------------*/
#include "stm32f1xx_hal.h"

/* Private includes ----------------------------------------------------------*/
/* USER CODE BEGIN Includes */
/* USER CODE END Includes */

/* Exported types ------------------------------------------------------------*/
/* USER CODE BEGIN ET */
extern ADC_HandleTypeDef hadc1;
extern I2C_HandleTypeDef hi2c1;
extern I2C_HandleTypeDef hi2c2;
extern RTC_HandleTypeDef hrtc;
extern SD_HandleTypeDef hsd;
extern SPI_HandleTypeDef hspi2;
extern UART_HandleTypeDef huart1; // debug log port
extern UART_HandleTypeDef huart2; // main uart port
extern DMA_HandleTypeDef hdma_sdio;
extern DMA_HandleTypeDef hdma_usart2_rx;
extern DMA_HandleTypeDef hdma_usart2_tx;
extern DMA_HandleTypeDef hdma_usart1_rx;
extern DMA_HandleTypeDef hdma_memtomem_dma1_channel1;
/* USER CODE END ET */

/* Exported constants --------------------------------------------------------*/
/* USER CODE BEGIN EC */

/* USER CODE END EC */

/* Exported macro ------------------------------------------------------------*/
/* USER CODE BEGIN EM */
// Configuration
#define IN_DEVELOPMENT 1 // Enable button-driven control, not missing any data.
#define HAS_DISPLAY 0     // SSD1306 is installed
#define FORWARD_MAIN_UART_TO_USB 1
#define HAS_USB_CDC_VCP 1 // enable virtual comm port
#define HAS_SD_CARD_IO 1  // Set 0 to make it compile faster for development.
#define BSP_W_USE_DMA 0     // enable the DMA W in bsp_driver_sd.c
#define BSP_R_USE_DMA 0     // enable the DMA R in bsp_driver_sd.c

/* USER CODE END EM */

/* Exported functions prototypes ---------------------------------------------*/
void Error_Handler(void);

/* USER CODE BEGIN EFP */

/* USER CODE END EFP */
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

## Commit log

2020-09-02 Initial commit, add hardware designs
    [Base_BOM_20191231.csv, Base_BOM_20200104.xlsx, Base_BOM_20200108.csv, Base_BOM_20200108.xlsx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]
2020-09-07 add readme to node mainboard
    [node_base.kicad_sch]
2020-09-08 Added materials, updated readme
    [Module Summary.xlsx]
2020-09-08 Added software folder, updated aux board readme
2022-01-25 Uploaded software codes
    [merge.csv, ra_info_merge.csv]

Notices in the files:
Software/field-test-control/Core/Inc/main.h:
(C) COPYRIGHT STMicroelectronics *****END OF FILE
